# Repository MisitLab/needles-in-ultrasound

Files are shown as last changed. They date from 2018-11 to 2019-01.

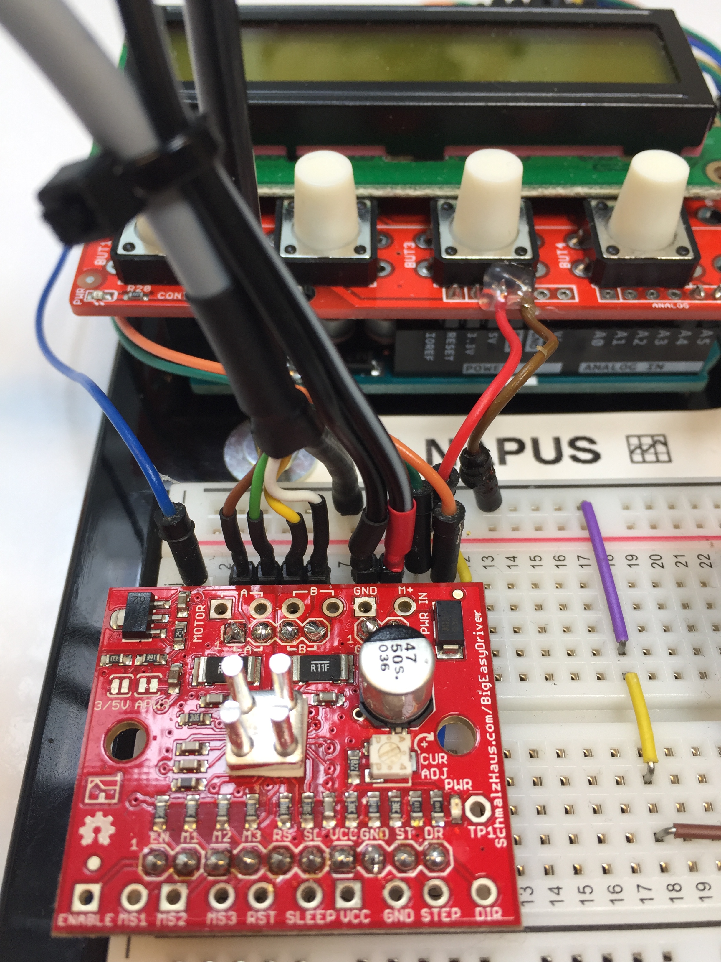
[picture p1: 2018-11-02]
Rotational platform control unit/Electronic design/Big Easy Driver wiring1.jpg

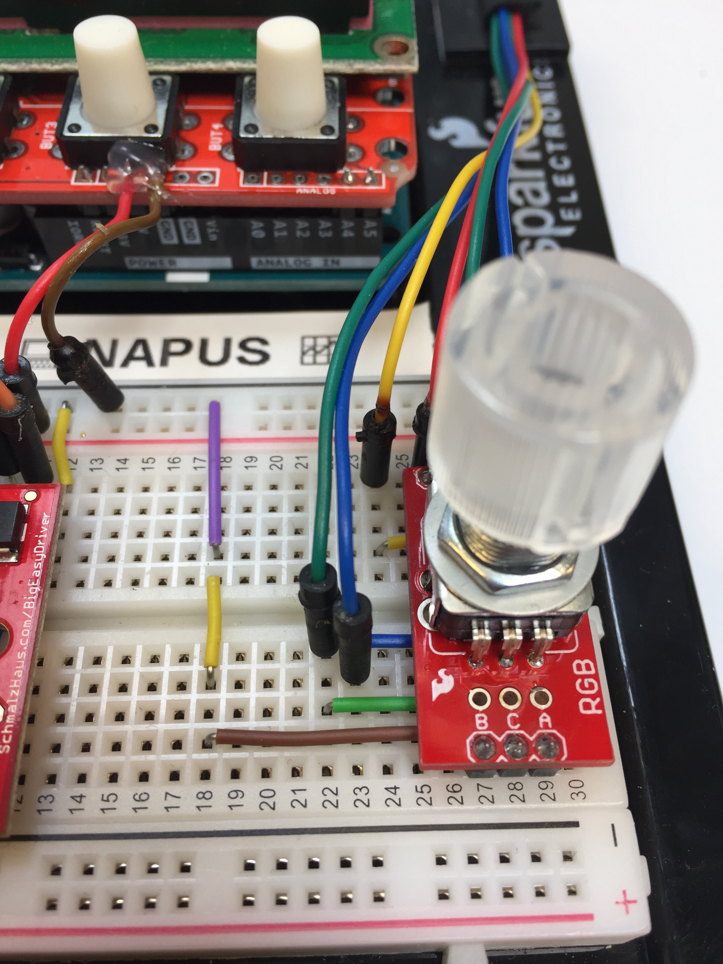
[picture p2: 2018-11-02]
Rotational platform control unit/Electronic design/Rotary Encoder wiring1.jpg

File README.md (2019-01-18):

# needles-in-ultrasound
## Welcome to the MISIT-lab Needles in Ultrasound GitHub page.
On this page you can find codes, processed data and relevant files that belong to the research study:

**Title**: A methodical quantification of needle visibility and echogenicity in ultrasound images.

**Authors**: Nick J. van de Berg, Juan A. Sánchez-Margallo, Arjan P van Dijke; Thomas Langø and John J van den Dobbelsteen.

**Journal**: Ultrasound in Medicine & Biology

**DOI**: https://doi.org/10.1016/j.ultrasmedbio.2018.10.004

**Youtube**: https://www.youtube.com/watch?v=cV3IzCwuDls

**License**: https://creativecommons.org/licenses/by-sa/4.0/

## Subdirectories:
**Data summary**: quick overview of data (Matlab)
- 'ech_collected_data.mat' contains needle echogenicity data,
- 'vis_collected_data.mat' contains needle visibility data,
- Run 'ech_data_show.m' or 'vis_data_show.m' to visualise the data.

**Image processing**: ultrasound video file analysis (Matlab)
- Run 'ech_improc.m' or 'vis_improc.m' to skip through the analysed ultrasound image frames,
- Examplar videos are added for code verification.

**Rotational platform control unit**: electronical parts and Arduino codes,
- 'Needles_in_Ultrasound_v1_2.ino' contains the Arduino code for the control unit,

**Rotational platform design**: mechanical parts.
- CAD models and purchased parts.

Note I: GitHub is not meant for data storage. Raw data (here: ultrasound videos, approx 7GB) are available upon request.

Note II: Bit rates of examplar video files were sometimes reduced to stay below the 25 MB limit. We do not guarantee equal video quality as the original files. Video quality did not reduce visibly.

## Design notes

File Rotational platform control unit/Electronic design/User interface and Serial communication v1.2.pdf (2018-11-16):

Needles in Ultrasound Project Nick van de Berg, Delft University of Technology

User Interface and Serial Communiction codes
v1.2 16 November 2018

diagram:

| | | --> | LCD |
| Arduino | | | | |
| | | <-- | UI |
^ | |
cmd| | |log
| | v
| MATLAB |

operation:
- set rotation angle and speed with buttons and LCD
- or: set rotation and speed over a serial link, e.g. from serial host (e.g. MATLAB)
- start and stop of movement with buttons, or by serial command from serial host
- Arduino logs over serial connection with event IDs (e.g. start, stop, settings programmed)

event-ID’s:

100 | <millis> | power on
101 | <millis> | motor on
102 | <millis> | motor off
103 | <millis> | motor stop requested
104 | <millis> | stepper disabled
120 | <millis> | serial synced
150 | <millis> | main menu
151 | <millis> | zero position mode
152 | <millis> | position mode
153 | <millis> | speed mode
154 | <millis> | speed and position mode
155 | <millis> | external mode
161 | <millis> | move to 0
162 | <millis> | make current position new 0
171 | <millis> | position set to,<pos>
172 | <millis> | speed set to,<speed>
901 | <millis> | impossible mode

serial commands:

! | sync byte from serial host
M x v | move (to_this_pos_x[d°], with_this_speed_v[d°/second])
V v | move (inf, with_this_speed_v[d°/second])
C1 | control(start): start movement
C0 | control(stop): stop movement
C5 | control(zero): make current position the new 0-position
C9 | control(release): disable stepper to move motor around freely

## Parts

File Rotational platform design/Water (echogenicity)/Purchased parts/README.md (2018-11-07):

Catalogues BLOCAN Profilsystems:

https://www.rk-rose-krieger.com/english/service/download-documents/catalogues/blocanr-profilsystems/

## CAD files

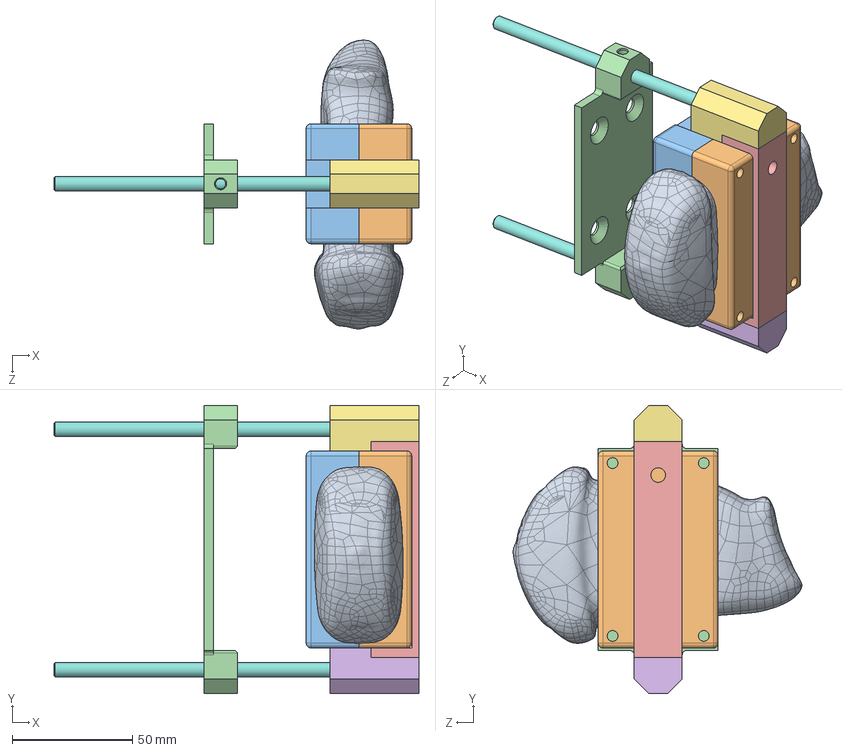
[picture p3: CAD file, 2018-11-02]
Rotational platform design/PVA (visibility)/Manufactured parts/Probe_Assembly_gel.SLDASM
152.0 x 120.0 x 120.3 mm
Probe
MoldLowerPart
MoldUpperPart
ProbeHolder_gel
ProbeSlider
Slider2Probeholder
Slider2Probeholder2
SliderAxis x 2

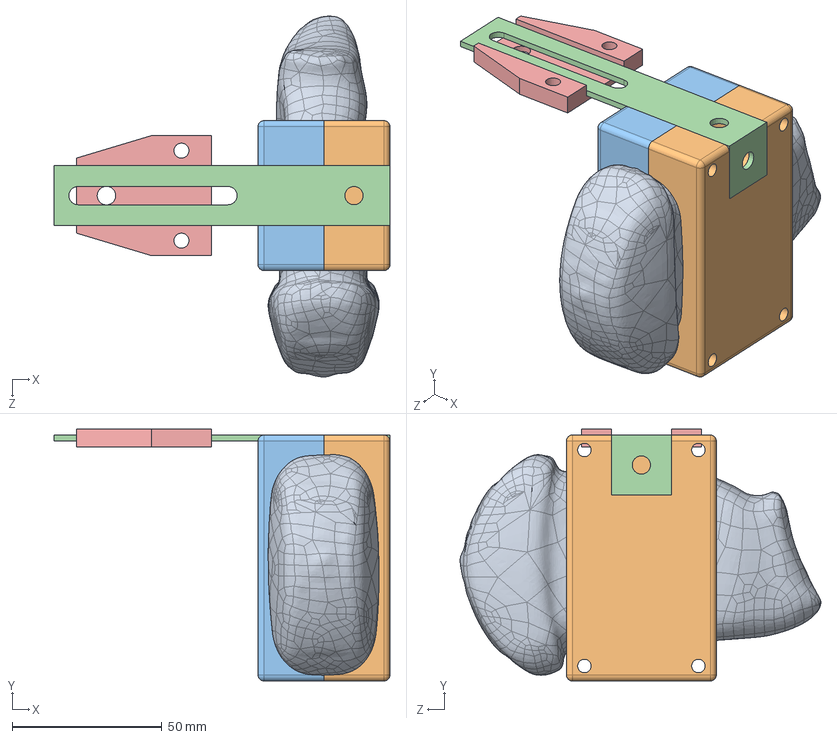
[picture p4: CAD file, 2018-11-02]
Rotational platform design/Water (echogenicity)/Manufactured parts/Probe_Assembly.SLDASM
112.0 x 84.0 x 120.3 mm
Probe
MoldLowerPart
MoldUpperPart
BracketElong
ProbeHolder

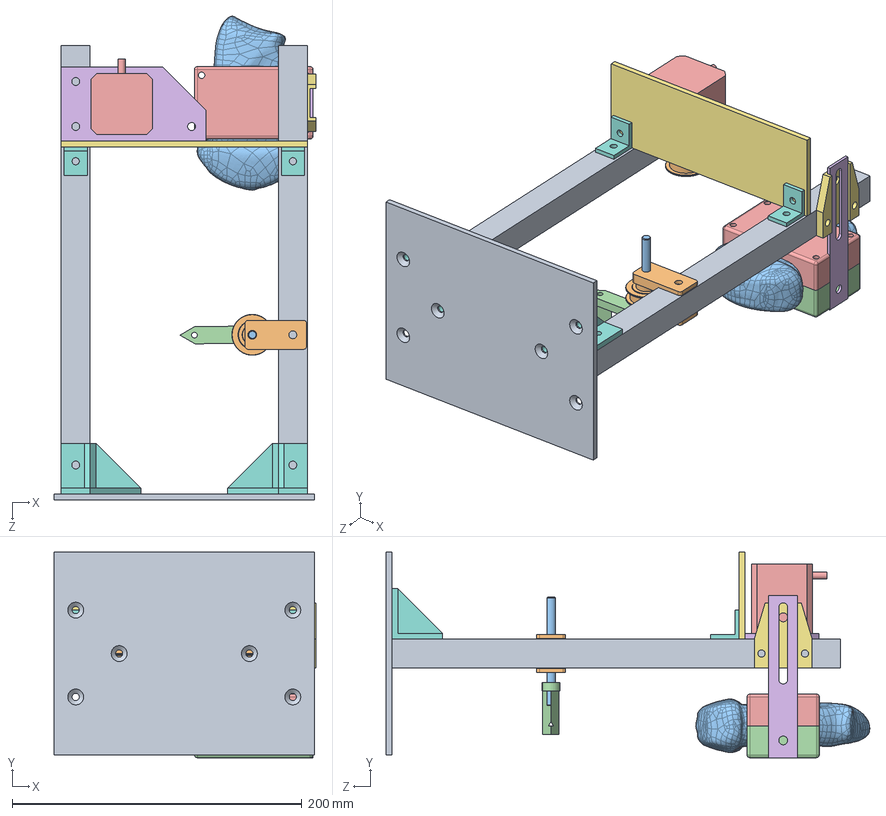
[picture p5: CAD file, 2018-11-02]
Rotational platform design/Water (echogenicity)/Manufactured parts/Assembly_Water.SLDASM
181.0 x 142.0 x 334.1 mm
Profile310 x 2
Pulley x 2
AxisPulley
NeedleHolder
StepperMotor
StepperMotorMount
StepperMotorCover
Connector_perp x 2
BaseSurface
PulleyConnector
Probe
MoldLowerPart
MoldUpperPart
BracketElong
ProbeHolder
CornerStone2 x 2

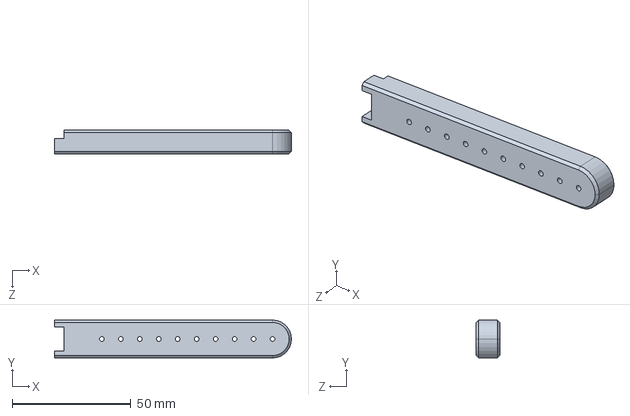
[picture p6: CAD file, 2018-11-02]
Rotational platform design/PVA (visibility)/Manufactured parts/NeedleTemplate.SLDPRT
100.0 x 16.0 x 10.0 mm

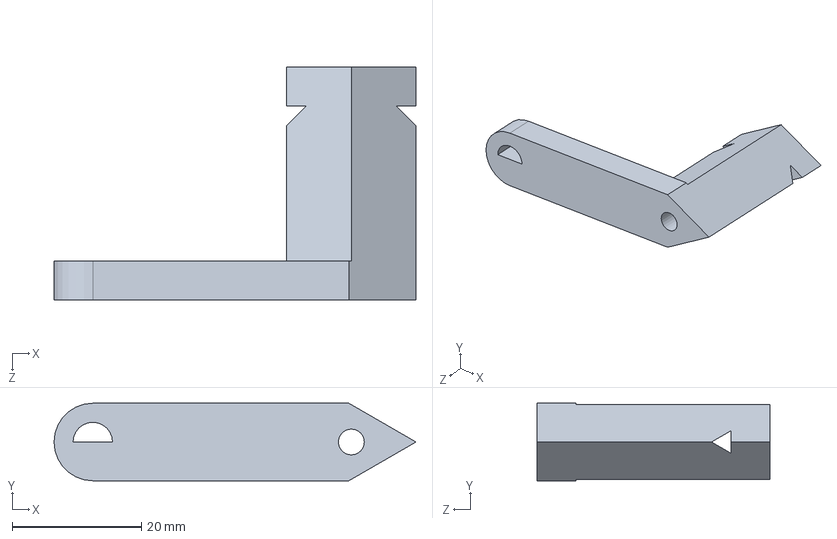
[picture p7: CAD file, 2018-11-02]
Rotational platform design/Water (echogenicity)/Manufactured parts/NeedleHolder.SLDPRT
56.0 x 12.0 x 36.0 mm

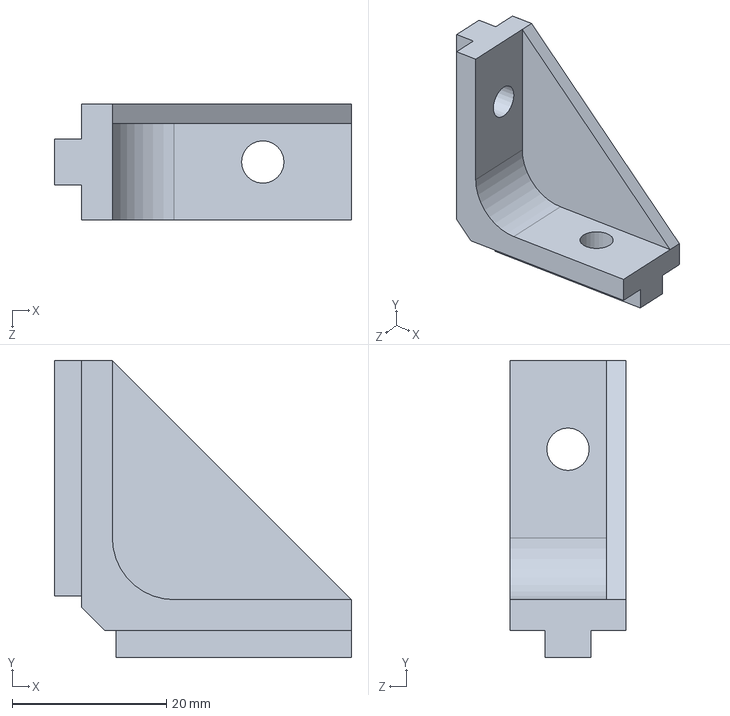
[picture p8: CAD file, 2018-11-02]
Rotational platform design/Water (echogenicity)/Manufactured parts/CornerStone.SLDPRT
38.5 x 38.5 x 15.0 mm

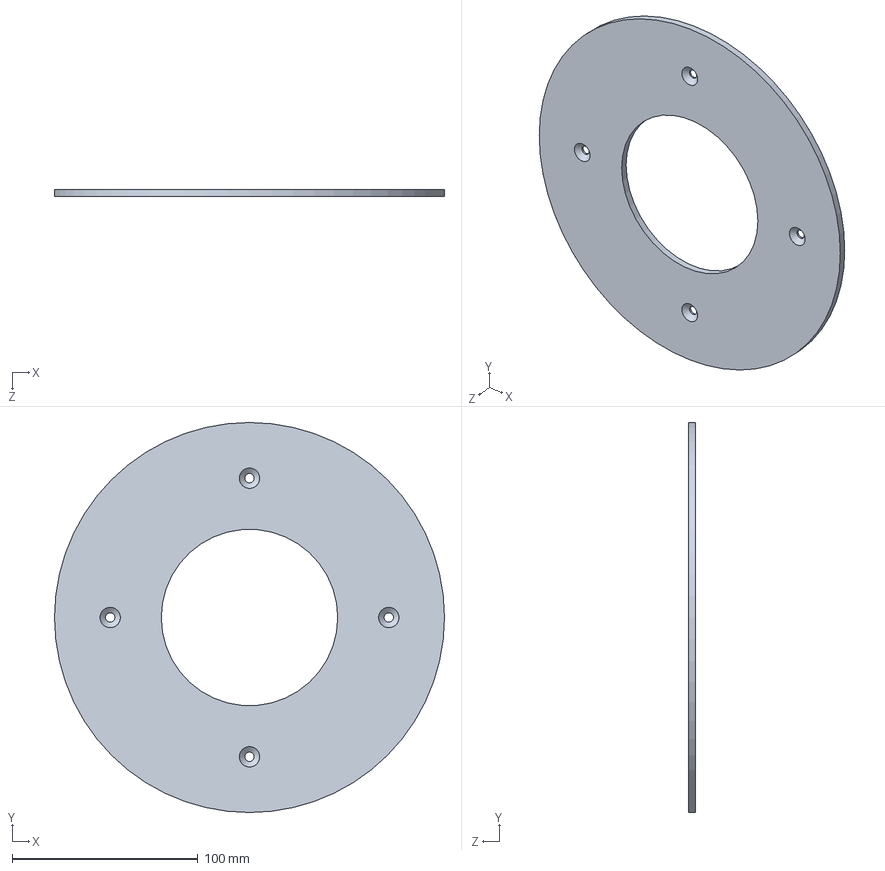
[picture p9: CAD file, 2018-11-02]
Rotational platform design/PVA (visibility)/Manufactured parts/RotarySupportPlate.SLDPRT
210.0 x 210.0 x 4.00 mm

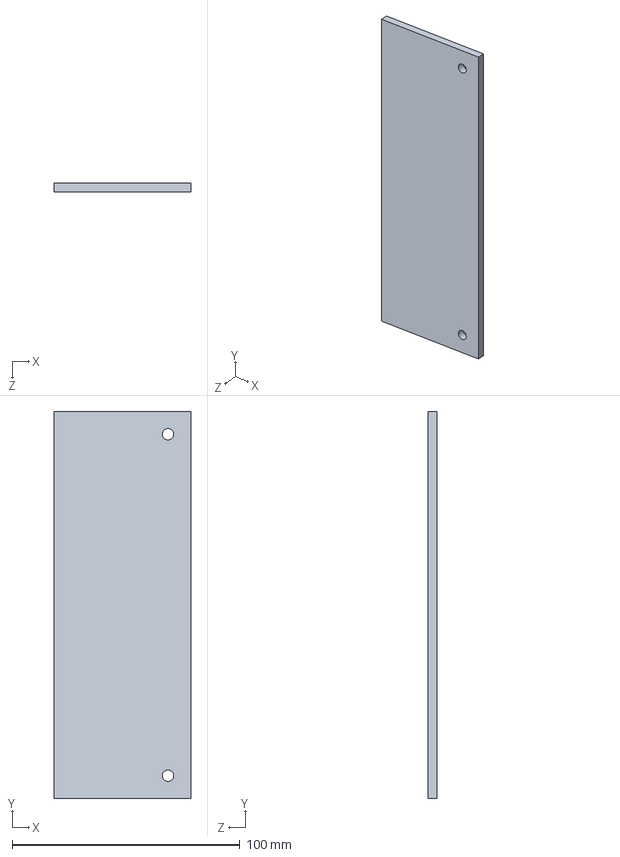
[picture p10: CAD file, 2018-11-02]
Rotational platform design/Water (echogenicity)/Manufactured parts/StepperMotorCover.SLDPRT
60.0 x 170.0 x 4.00 mm

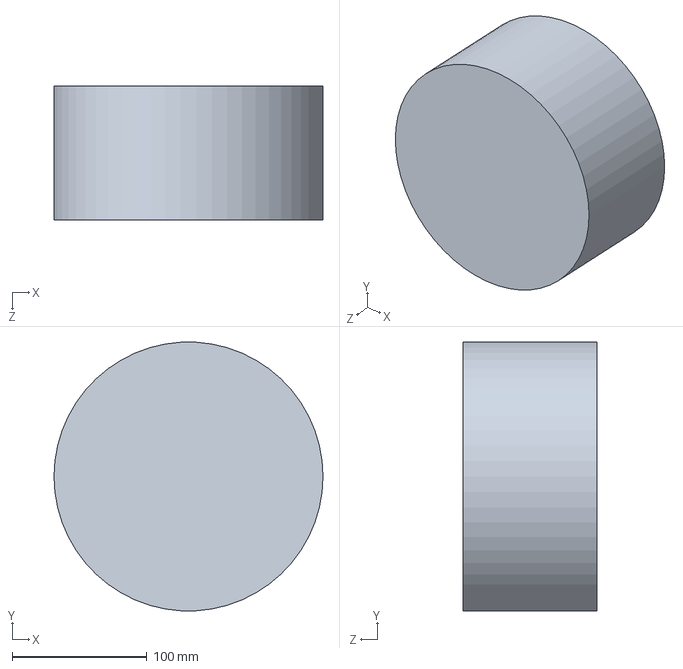
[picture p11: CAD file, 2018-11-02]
Rotational platform design/PVA (visibility)/Manufactured parts/GelBlock.SLDPRT
200.0 x 199.7 x 100.0 mm

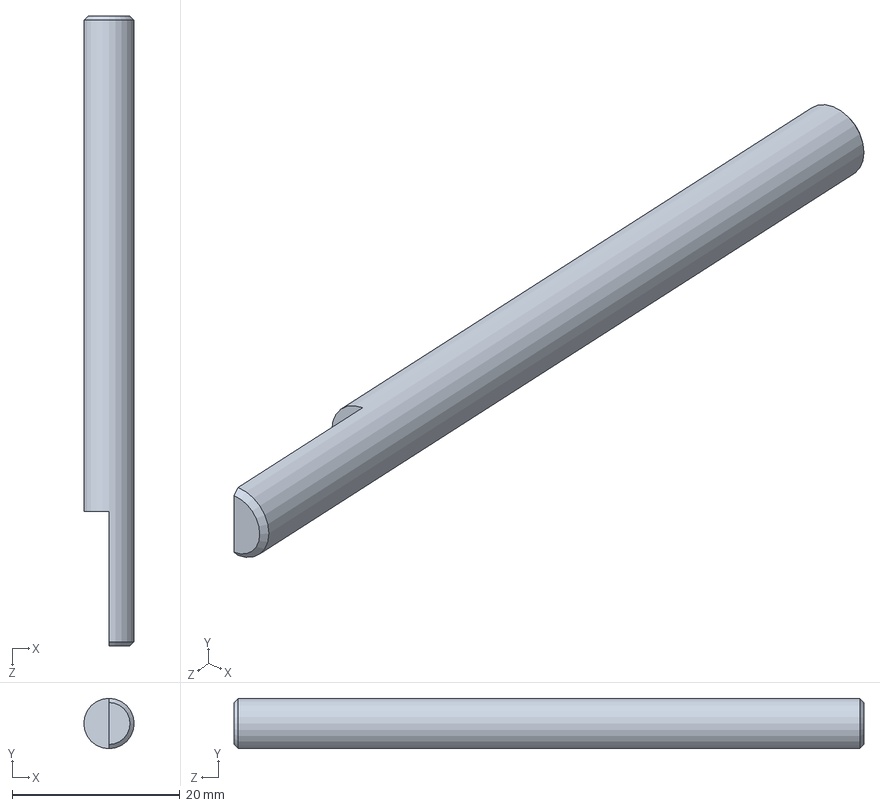
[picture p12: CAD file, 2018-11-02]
Rotational platform design/Water (echogenicity)/Manufactured parts/AxisPulley.SLDPRT
6.00 x 6.00 x 75.0 mm

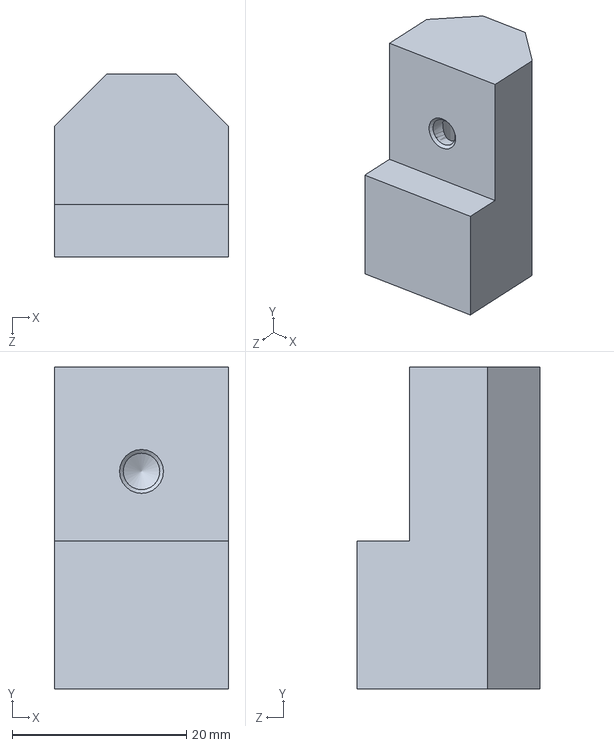
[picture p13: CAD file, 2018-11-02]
Rotational platform design/PVA (visibility)/Manufactured parts/Slider2Probeholder2.SLDPRT
20.0 x 37.0 x 21.0 mm

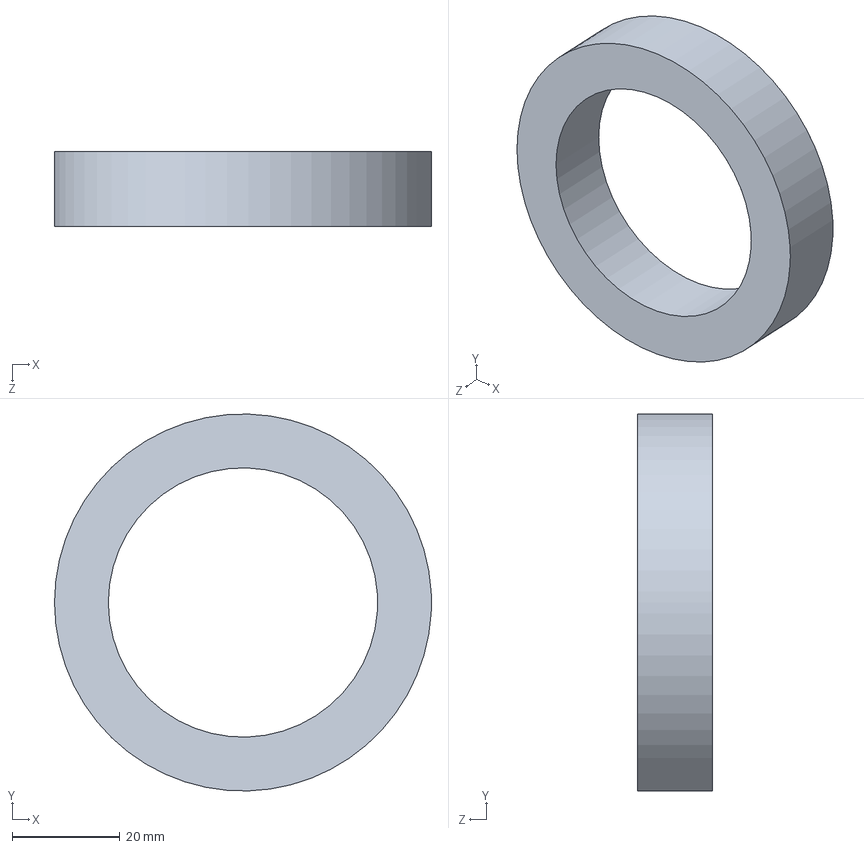
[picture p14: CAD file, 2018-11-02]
Rotational platform design/PVA (visibility)/Manufactured parts/Bearing.SLDPRT
70.0 x 70.0 x 14.0 mm

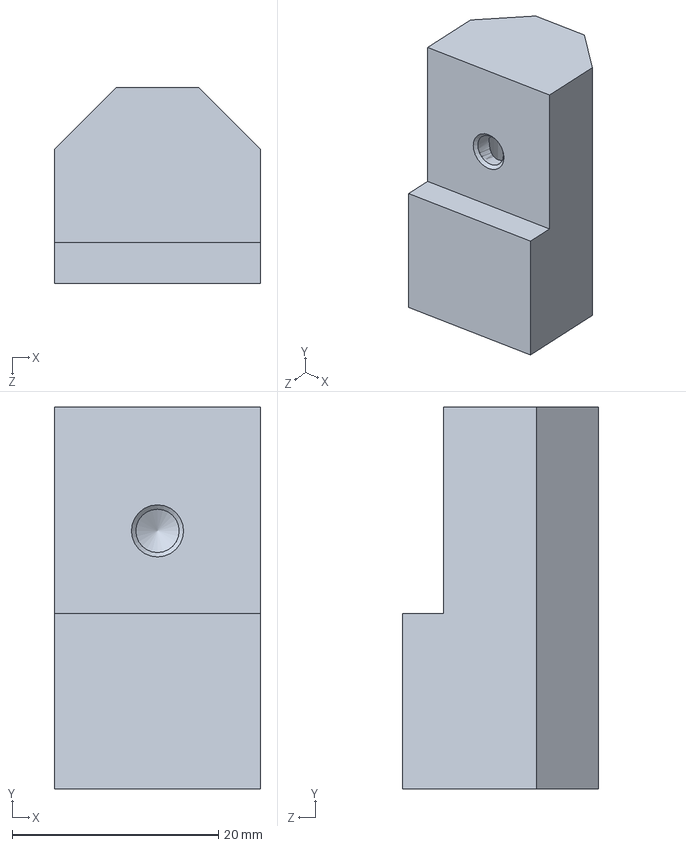
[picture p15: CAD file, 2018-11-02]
Rotational platform design/PVA (visibility)/Manufactured parts/Slider2Probeholder.SLDPRT
20.0 x 37.0 x 19.0 mm

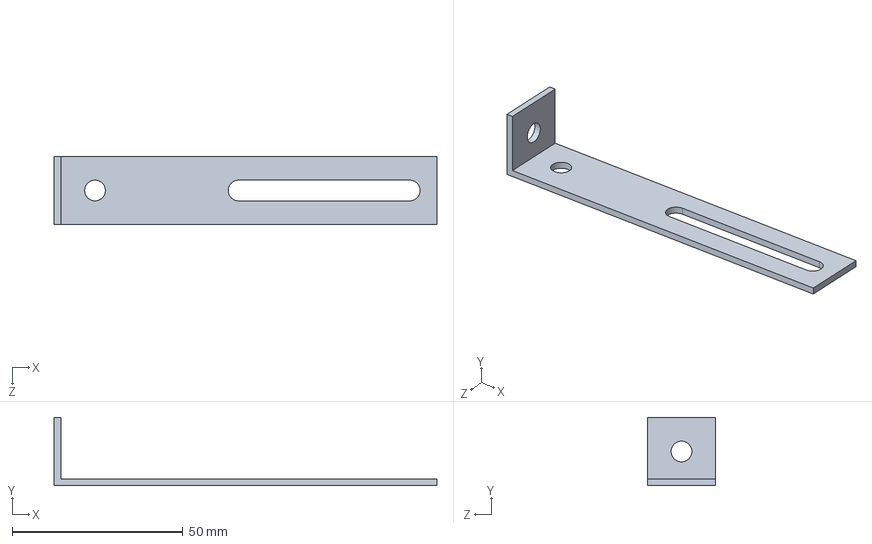
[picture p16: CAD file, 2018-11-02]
Rotational platform design/Water (echogenicity)/Manufactured parts/BracketElong.SLDPRT
112.0 x 20.0 x 20.0 mm

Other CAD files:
Rotational platform design/Water (echogenicity)/Manufactured parts/NeedleHolder_forprinting.STL
Rotational platform design/PVA (visibility)/Manufactured parts/Profile60.SLDPRT
Rotational platform design/Water (echogenicity)/Manufactured parts/ProbeHolder_forprinting.STL
Rotational platform design/PVA (visibility)/Manufactured parts/BearingFixture.SLDPRT
Rotational platform design/PVA (visibility)/Manufactured parts/MicroStageFixture.SLDPRT
Rotational platform design/PVA (visibility)/Manufactured parts/MoldLowerPart.sldprt
Rotational platform design/PVA (visibility)/Manufactured parts/MoldUpperPart.sldprt
Rotational platform design/PVA (visibility)/Manufactured parts/ProbeHolder_gel.SLDPRT
Rotational platform design/PVA (visibility)/Manufactured parts/Profile65.SLDPRT
Rotational platform design/PVA (visibility)/Manufactured parts/RotarySupportPlate_forlasercutting.DXF
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

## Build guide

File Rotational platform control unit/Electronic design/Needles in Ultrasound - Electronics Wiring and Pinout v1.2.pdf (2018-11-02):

### Electronics Wiring Schematic and Pinout - Needles‐in‐Ultrasound

version 1.2 ‐ 26 March 2018
Nick van de Berg, Arjan van Dijke, Delft University of Technology https://github.com/MisitLab/needles-in-ultrasound

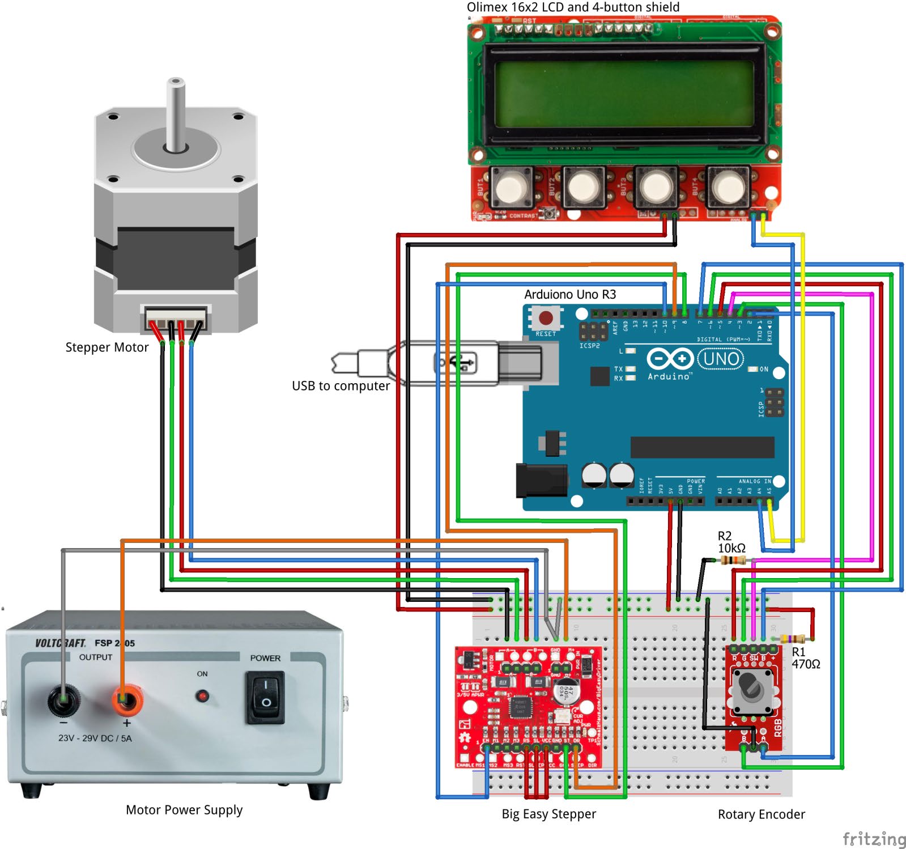
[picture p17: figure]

Components:
- Arduino Uno Rev3 (A000066)
https://store.arduino.cc/arduino-uno-rev3
- Olimex LCD Shield 16x2 (SHIELD-LCD16x2) https://www.olimex.com/Products/Duino/Shields/SHIELD-LCD16x2/open-source-hardware
- Sparkfun Big Easy Driver (ROB-12859)
https://www.sparkfun.com/products/12859
- Sparkfun Illuminated Rotary Encoder on breakout board (COM-10982 + BOB-11722) https://www.sparkfun.com/products/10982https://www.sparkfun.com/products/11722
- WanTai Motor 42BYGHM809 Hybrid Bipolar Stepper Motor http://www.wantmotor.com/product/42byghm.html
- USB 5V power from computer for Arduino
- Lab 24V power supply for motor
| wire color | connected to
Arduino Uno pinout:
0. -
1. -
2. rotary encoder A (interrupt) blue | Rotary Encoder pin A
3. rorary encoder B (interrupt) green | Rotary Encoder pin B
4. rotary pushbutton | pink | Rotary Encoder SW
5. LED red | red | Rotary Encoder LED R
6. LED green | green | Rotary Encoder LED G
7. LED blue | blue | Rotary Encoder LED B
8. motor step | green | Big Easy driver STEP
9. motor dir | orange | Big Easy driver DIR
10. motor enable | blue | Big Easy driver EN
11. -
12. -
13. (built-in LED)
A0.
A1.
A2.
A3.
A4. I2C SDA | blue | LCD Shield SDA
A5. I2C SCL | yellow | LCD Shield SCL
5V. 5V power | red | 5V line (rail) on breadboard
GND. ground | black | GND line (rail) on breadboard

Motor signal cable pinout:
Big Easy | wire color | connected to
A+ | black | Stepper Motor A+
A- | green | Stepper Motor A-
B+ | red | Stepper Motor B+
B- | blue | Stepper Motor B-

Motor power cable pinout:
Big Easy | wire color | connected to
M+ | orange | Motor Power Supply +
GND | grey | Motor Power Supply GND & GND line (rail) on breadboard

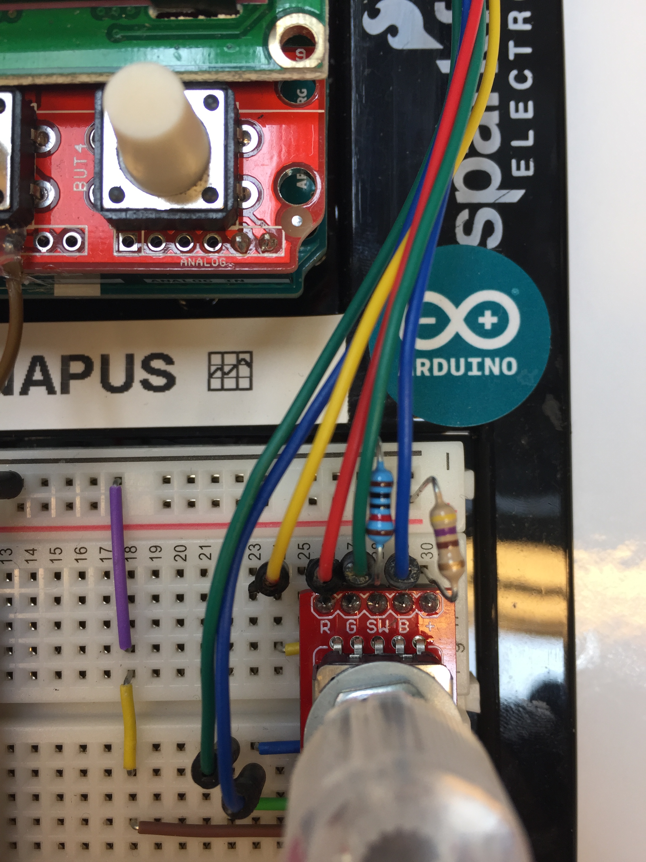
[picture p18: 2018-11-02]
Rotational platform control unit/Electronic design/Rotary Encoder wiring2.jpg

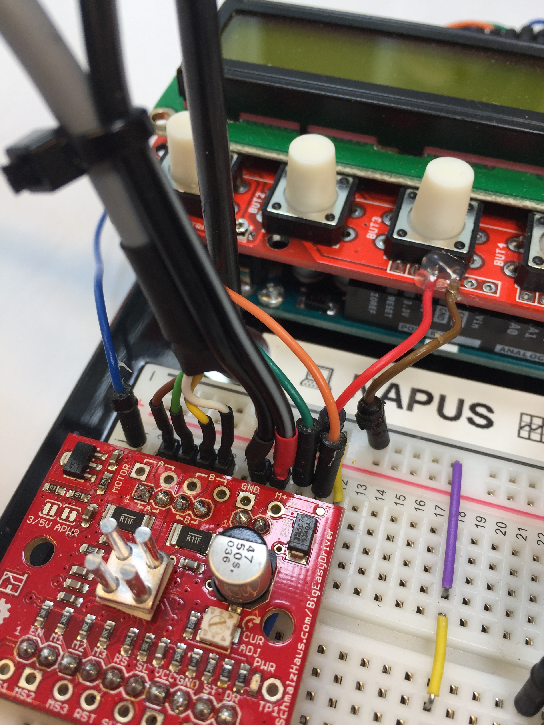
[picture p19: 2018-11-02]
Rotational platform control unit/Electronic design/Big Easy Driver wiring2.jpg

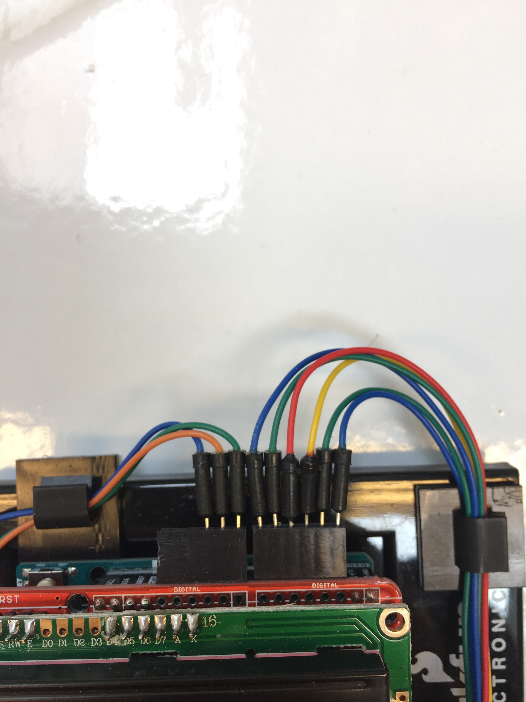
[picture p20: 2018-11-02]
Rotational platform control unit/Electronic design/Olimex Shield wiring.jpg

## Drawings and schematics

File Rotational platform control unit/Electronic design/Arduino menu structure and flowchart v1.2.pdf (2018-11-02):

## Menu Structure & Flowchart Needles‐in‐Ultrasound

### version 1.2 ‐ 2 March 2018

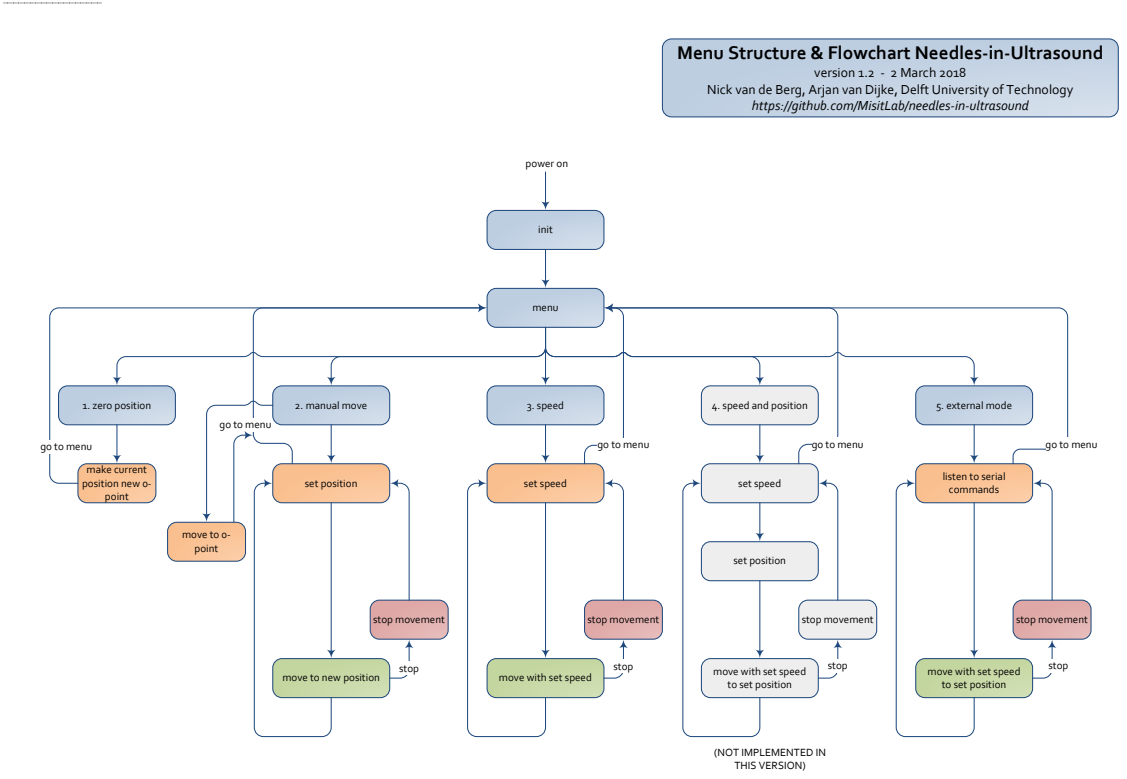
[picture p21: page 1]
init; power on; menu; 2. manual move; 3. speed; move to 0‐ point; set position; set speed; stop movement; stop; 1. zero position; 5. external mode; make current position new 0‐ point; go to menu

Nick van de Berg, Arjan van Dijke, Delft University of Technology

https://github.com/MisitLab/needles‐in‐ultrasound

4. speed and position

go to menu

listen to serial
commands

move to new position

move with set speed

to set position

(NOT IMPLEMENTED IN
THIS VERSION)

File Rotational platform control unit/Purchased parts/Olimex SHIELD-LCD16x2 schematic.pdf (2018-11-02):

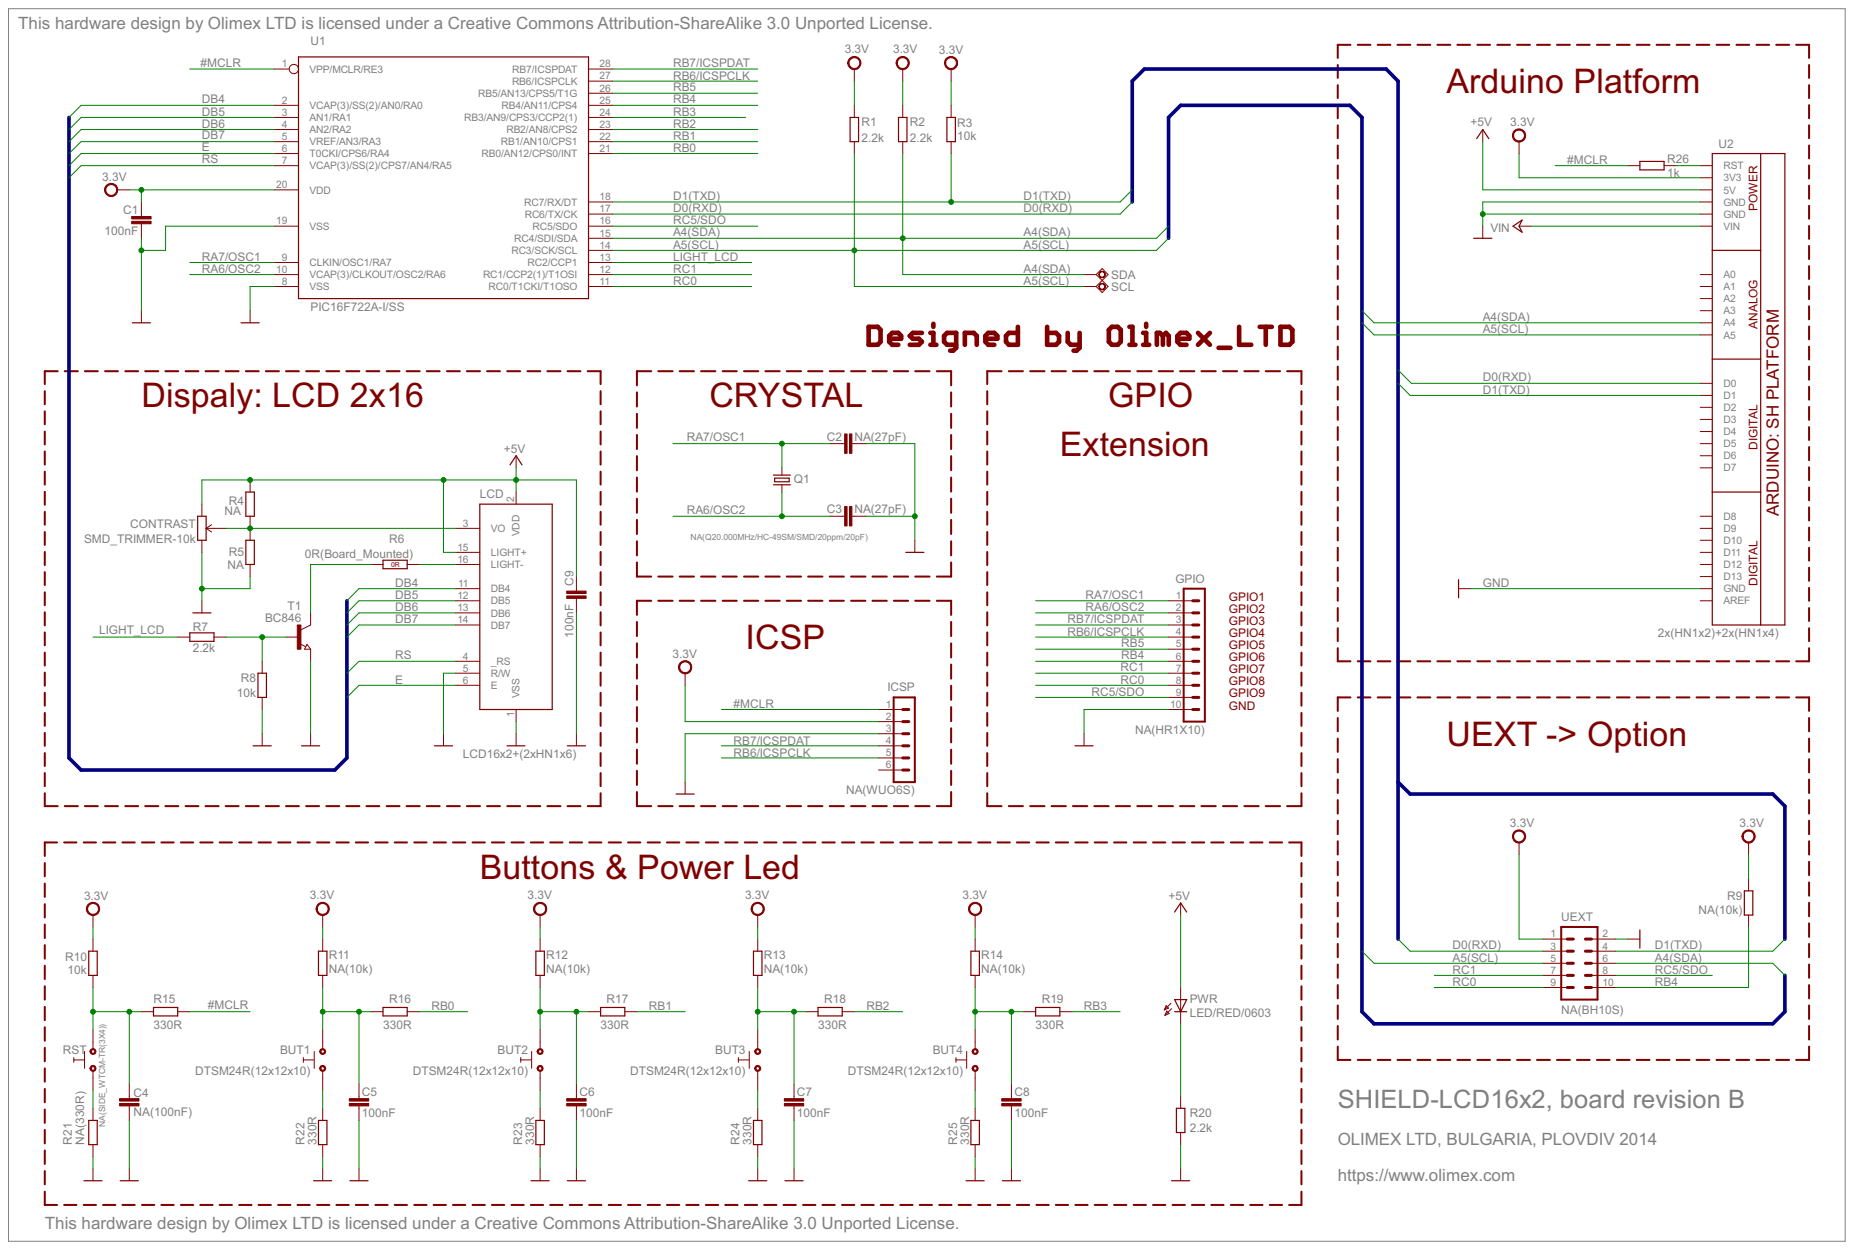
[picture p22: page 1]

This hardware design by Olimex LTD is licensed under a Creative Commons Attribution-ShareAlike 3.0 Unported License.

POWER ANALOG DIGITAL DIGITAL ARDUINO: SH PLATFORM

NA(Q20.000MHz/HC-49SM/SMD/20ppm/20pF) NA(27pF)
RA6/OSC2

OLIMEX LTD, BULGARIA, PLOVDIV 2014

https://www.olimex.com

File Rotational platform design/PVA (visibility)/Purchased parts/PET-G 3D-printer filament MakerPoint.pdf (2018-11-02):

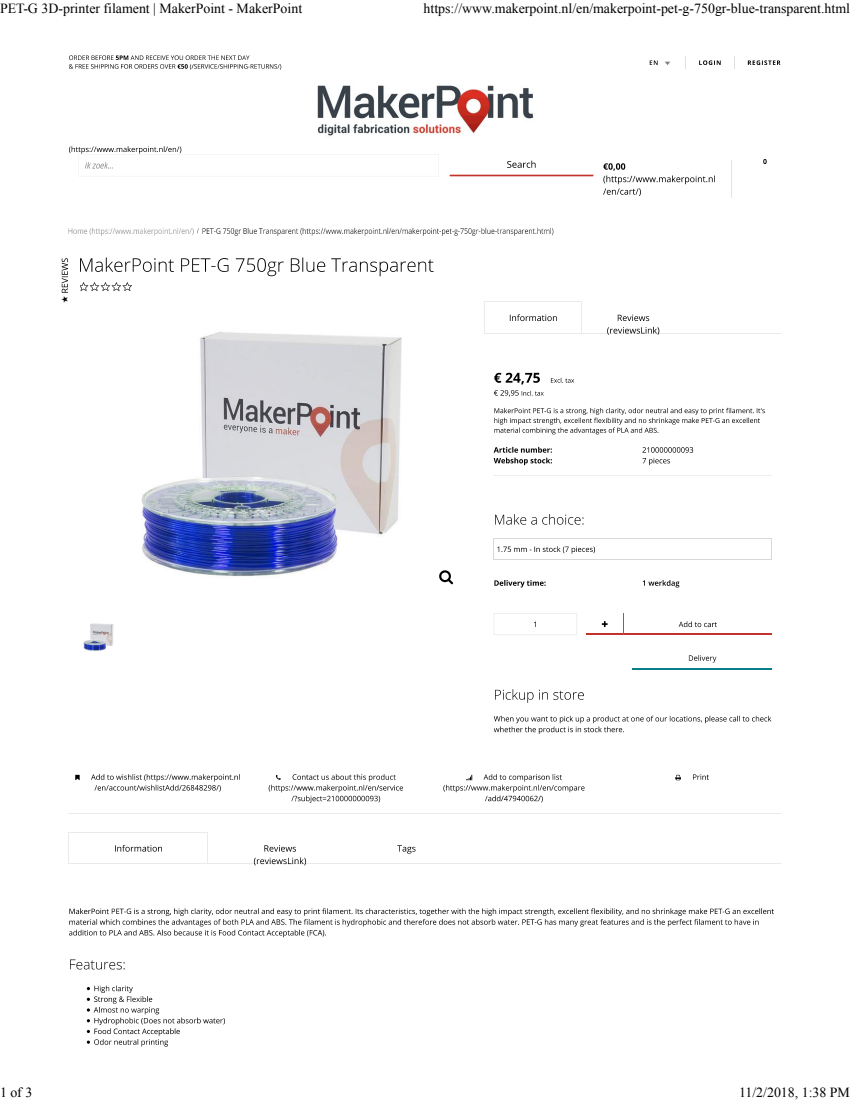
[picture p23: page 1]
PET-G 3D-printer filament | MakerPoint - MakerPoint; https://www.makerpoint.nl/en/makerpoint-pet-g-750gr-blue-transparent.html

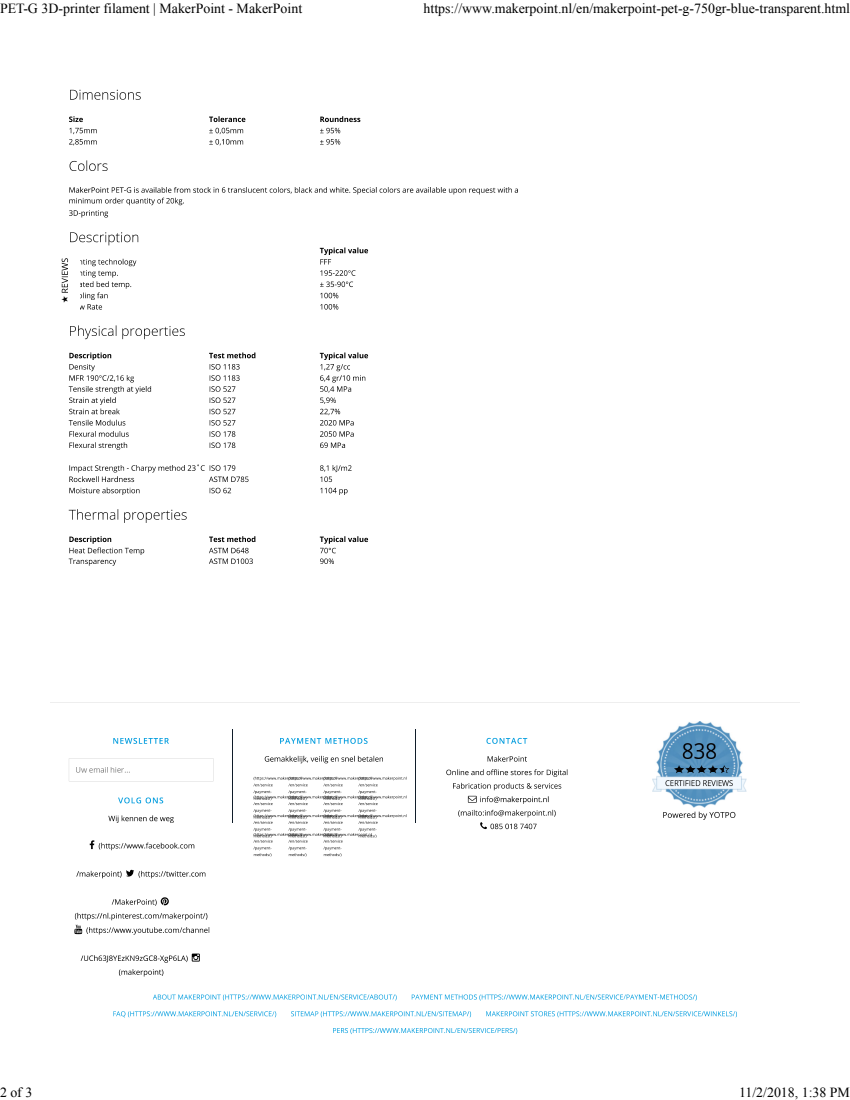
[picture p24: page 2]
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

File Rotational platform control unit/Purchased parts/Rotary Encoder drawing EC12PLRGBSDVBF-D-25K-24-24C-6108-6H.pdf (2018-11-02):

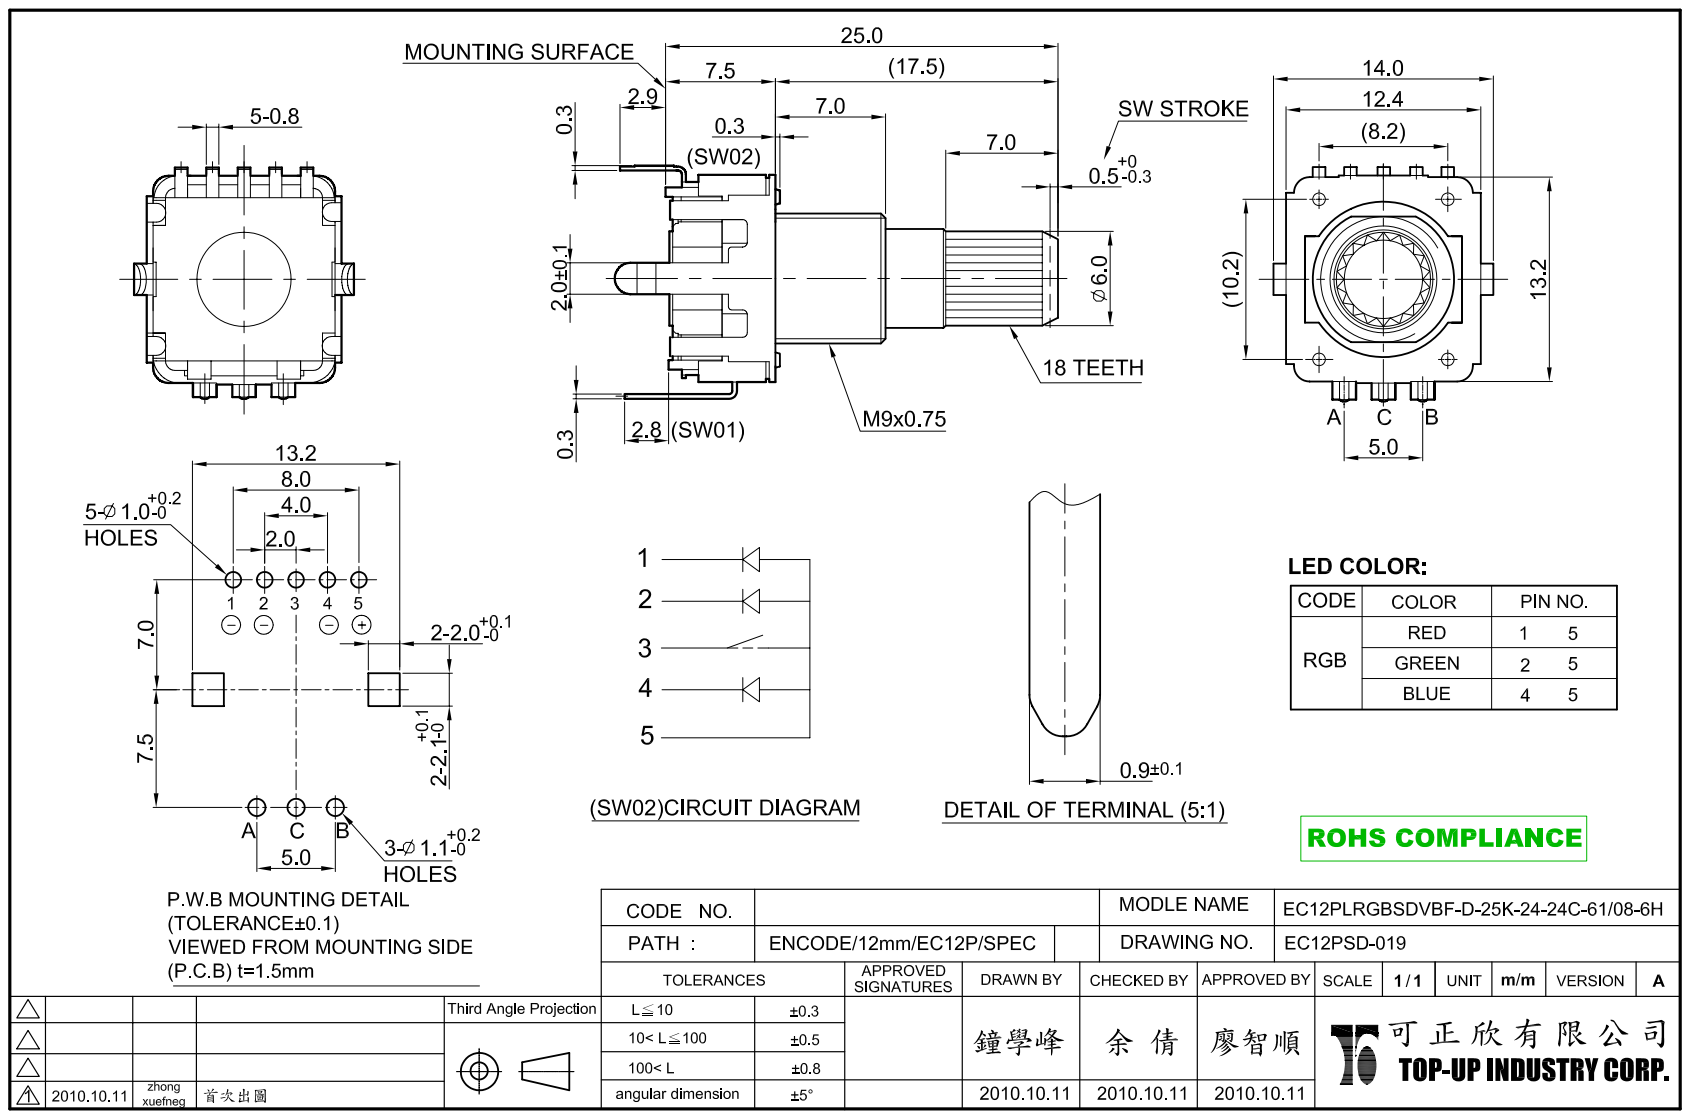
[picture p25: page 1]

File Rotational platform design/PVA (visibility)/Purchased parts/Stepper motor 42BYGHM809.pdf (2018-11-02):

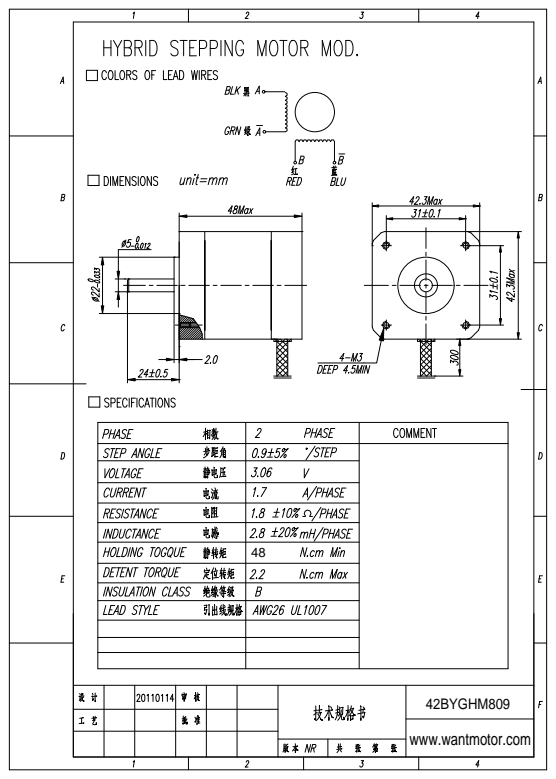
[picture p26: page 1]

42BYGHM809
www.wantmotor.com

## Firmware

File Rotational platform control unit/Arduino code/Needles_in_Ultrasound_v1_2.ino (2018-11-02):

// *****************************************************************
/*
  Needles In Ultrasound

  Firmware for the Arduino-based controller
  for the Needles In Ultasound setup from Nick van de Berg, Delft University of Technology

  by Arjan van Dijke - A.P.vanDijke@tudelft.nl
  and Nick van de Berg - N.J.P.vandeBerg@tudelft.nl
  
  MISIT - www.misit.nl
  BioMechanical Engineering
  Delft University of Technology

  hardware used:
  - Arduino Uno Rev3
    https://store.arduino.cc/arduino-uno-rev3
  - SparkFun Big Easy stepper driver + NEMA17 stepper motor
    https://www.sparkfun.com/products/12859
  - SparkFun Rotary Knob
    https://www.sparkfun.com/products/10982
  - Olimex 16x2 LCD Shield
    https://www.olimex.com/Products/Duino/Shields/SHIELD-LCD16x2/

  software used:
  - Arduino IDE 1.8.5
    https://www.arduino.cc/en/Main/Software
  - Wire library, inluded in Arduino IDE
    https://www.arduino.cc/en/Reference/Wire
  - Olimex LCD16x2 library v1.0
    https://www.olimex.com/Products/Duino/Shields/SHIELD-LCD16x2/open-source-hardware
  - AccelStepper library v1.57.1
    http://www.airspayce.com/mikem/arduino/AccelStepper/

  for the Arduino pinout, see: Arduino pinout NAPUS vx.x.docx
  for the menu structure and flowchart, see: Arduino flowchart and menu structure NAPUS vx.x.vsd
  for the project design agreements, see Design agreements NAPUS -version-.docx
*/

  String firmwareversion = "v1.2";

/*    
  changelog:
    v1.2 - 12 April 2018 - added external (Matlab) control and code cleanup for publication
    v1.1 - 20 April 2017 - fixes to 0-ing position
    v1.0 - 23 March 2017 - initial version

*/
// *****************************************************************



// *****************************************************************
// includes
// *****************************************************************
#include <Wire.h>
#include <LCD16x2.h>
#include <AccelStepper.h>



// *****************************************************************
// defines
// *****************************************************************
#define SERIALBAUDRATE 115200   // serial link (usb) baudrate
#define MANUALMOVESPEED 100     // manual move speed in pulses per second
#define MANUALMOVESPEEDG 56     // manual move speed in 10th of degrees per second (steps*360/640)
#define ROTA 2                  // rotary knob pin A
#define ROTB 3                  // rotary knob pin B
#define PUSHBUTTON 4            // rotary knob push button
#define LEDR 5                  // multicolor LED in rotary knob - red
#define LEDG 6                  // multicolor LED in rotary knob - green
#define LEDB 7                  // multicolor LED in rotary knob - blue
#define MOTORSTEP 8             // the stepper motor step pin
#define MOTORDIR 9              // the stepper motor direction pin
#define MOTOREN 10              // the stepper motor enable pin



// *****************************************************************
// variables
// *****************************************************************

// LCD and buttons
LCD16x2 lcd;                    // the LCD shield
char lcdprintbuffer[17];        // buffer for holding printable chars on lcd (16 chars + trailing 0)
byte lcdbuttons;                // to store button state from lcd
boolean button1 = false;        // to store button states
boolean button2 = false;
boolean button3 = false;
boolean button4 = false;

// stepper motor and driver
AccelStepper stepper(AccelStepper::DRIVER, MOTORSTEP, MOTORDIR);   // BigEasy driver on pin MOTORSTEP and MOTORDIR

// rotary knob
// got this from bildr article: http://bildr.org/2012/08/rotary-encoder-arduino/
volatile int lastEncoded = 0;
volatile long encoderValue = 0;     // position of motor in steps
long previousEncoderValue = 0;
volatile long encoderAngle = 0;     // position in motor in 10th of degrees
long previousEncoderAngle = 0;
int lastMSB = 0;
int lastLSB = 0;

// menu items
byte currentmode = 2;           // to store the menu mode (1=zero position, 2=manual move, 3=speed, 4=speed and position, 5=external)
byte previousmode = 0;          // to remember the previous selected mode
boolean showmenu = true;        // flag to indicate if we want to make new settings in the menu

// serial logging
boolean doseriallogging = true;                     // flag to set if we want serial log events
boolean menueventlogged = false;                    // flag to store if we logged the menu entry event
boolean modeeventlogged = false;                    // flag to store if we logged the mode entry event

// serial input
byte inChar;                    // var to store incoming serial characters
long serialPositionG;           // serial read position setting in deci-degrees
long serialPositionP;           // serial read position setting in pulses
long serialSpeedG;              // serial read speed setting in deci-degrees
long serialSpeedP;              // serial read speed setting in pulses
char serialMode;                // 'U' for undefined, 'M' for movement(pos,speed) or 'V' for movement(speed)
boolean externalmode_exit = false;  // flag to exit run loops with C0


// *****************************************************************
// encoder interrupt handler
// *****************************************************************
void updateEncoder() {
  int MSB = digitalRead(ROTA); // MSB = most significant bit
  int LSB = digitalRead(ROTB); // LSB = least significant bit

  int encoded = (MSB << 1) |LSB; // converting the 2 pin value to single number
  int sum  = (lastEncoded << 2) | encoded; // adding it to the previous encoded value

  if(sum == 0b1101 || sum == 0b0100 || sum == 0b0010 || sum == 0b1011) encoderAngle = encoderAngle + 5;    // increase angle
  if(sum == 0b1110 || sum == 0b0111 || sum == 0b0001 || sum == 0b1000) encoderAngle = encoderAngle - 5;    // decrease angle

  lastEncoded = encoded; //store this value for next time
}



// *****************************************************************************
// LED on-off functions, to avoid confusing non deinverting negative unlogic
// *****************************************************************************
void ledred(byte ledstate) {
  switch (ledstate) {
    case 0:
      digitalWrite(LEDR, HIGH);  // switch off red led with inverted logic
      break;
    case 1:
      digitalWrite(LEDR, LOW);   // switch on red led with inverted logic
      break;
    default:
      break;
  }
}

void ledgreen(byte ledstate) {
  switch (ledstate) {
    case 0:
      digitalWrite(LEDG, HIGH);  // switch off green led with inverted logic
      break;
    case 1:
      digitalWrite(LEDG, LOW);   // switch on green led with inverted logic
      break;
    default:
      break;
  }
}

void ledblue(byte ledstate) {
  switch (ledstate) {
    case 0:
      digitalWrite(LEDB, HIGH);  // swtich off blue led with inverted logic
      break;
    case 1:
      digitalWrite(LEDB, LOW);   // switch on blue led with inverted logic
      break;
    default:
      break;
  }
}



// *****************************************************************************
// seriallog: serial prints event ids, milliseconds, and human readable string
// *****************************************************************************

// prototype the function to allow optional arguments
void seriallog (byte eventid, long extradata1 = 0, long extradata2 = 0);

// define the function
void seriallog (byte eventid, long extradata1 = 0, long extradata2 = 0) {

  if (doseriallogging) {
    Serial.print(eventid);                            // print event id
    Serial.print(",");
    Serial.print(millis());                           // print current millis()
    Serial.print(",");
    switch (eventid) {                                // print human readable string
      case 100: Serial.println("NAPUS power on"); break;
      case 101: Serial.println("motor on"); break;
      case 102: Serial.println("motor off"); break;
      case 103: Serial.println("motor stop requested"); break;
      case 104: Serial.println("stepper disabled"); break;
      case 120: Serial.println("serial synced"); break;
      case 150: Serial.println("main menu"); break;
      case 151: Serial.println("zero position mode"); break;
      case 152: Serial.println("position mode"); break;
      case 153: Serial.println("speed mode"); break;
      case 154: Serial.println("speed and position mode"); break;
      case 155: Serial.println("external mode"); break;
      case 161: Serial.println("move to 0"); break;
      case 162: Serial.println("make current position new 0"); break;
      case 171:
        Serial.print("position set to,");
        Serial.print(extradata1);                     // position in 10ths of degrees
        Serial.print(",");
        Serial.println(extradata2);                   // position in steps
        break;
      case 172:
        Serial.print("speed set to,");
        Serial.print(extradata1);                     // speed in in 10ths of degrees per second
        Serial.print(",");
        Serial.println(extradata2);                   // speed in steps per second
        break;
      case 901: Serial.println("impossible mode"); break;
      default: Serial.println("unknown event");
    } // end switch
  } // end if doseriallogging
}




// *****************************************************************
// setup
//   "He who fails to prepare, prepares to fail." (Confucius)
// *****************************************************************
void setup() {

  // setup Serial link
  Serial.begin(SERIALBAUDRATE);

  // setup I2C
  Wire.begin();

  // setup LCD
  lcd.lcdClear();                                     // clear screen
  lcd.lcdSetBlacklight(80);                           // LCD backlight on
  
  // show name and version on lcd
  lcd.lcdGoToXY(1,1);                                 // line 1 position 1
  //            0123456789012345
  lcd.lcdWrite(" Needles-in-US");
  lcd.lcdGoToXY(7,2);                                 // line 2 position 7
  firmwareversion.toCharArray(lcdprintbuffer,16);     // put versionstring in lcdprintbuffer
  lcd.lcdWrite(lcdprintbuffer);                       // and print it on LCD
  delay(3000);
  lcd.lcdClear();                                     // clear LCD

  // rotary knob
  pinMode(ROTA, INPUT_PULLUP); 
  pinMode(ROTB, INPUT_PULLUP);
  pinMode(PUSHBUTTON, INPUT);                         // INPUT, because it has its own (hardware) pulldown
  attachInterrupt(0, updateEncoder, CHANGE);          // attach interrupt to ROTA, call handler on change of the signal
  attachInterrupt(1, updateEncoder, CHANGE);          // attach interrupt to ROTB, call handler on change of the signal

   // LEDs
  pinMode(LEDR, OUTPUT);
  ledred(0);                                          // red led OFF at startup
  pinMode(LEDG, OUTPUT);
  ledgreen(0);                                        // green led OFF at startup
  pinMode(LEDB, OUTPUT);
  ledblue(1);                                         // blue led ON at startup

  // stepper
  stepper.setPinsInverted(false,false,true);          // direction normal, step normal, enable inverted
  stepper.setEnablePin(MOTOREN);                      // set motor enable pin
  stepper.setMaxSpeed(1000);                          // max speed of the stepper
  stepper.setAcceleration(100);                       // max acceleration of the stepper
  stepper.disableOutputs();                           // disable stepper at startup (!)

  // log event
  seriallog(100);                                     // event 100: NAPUS power on

}
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
